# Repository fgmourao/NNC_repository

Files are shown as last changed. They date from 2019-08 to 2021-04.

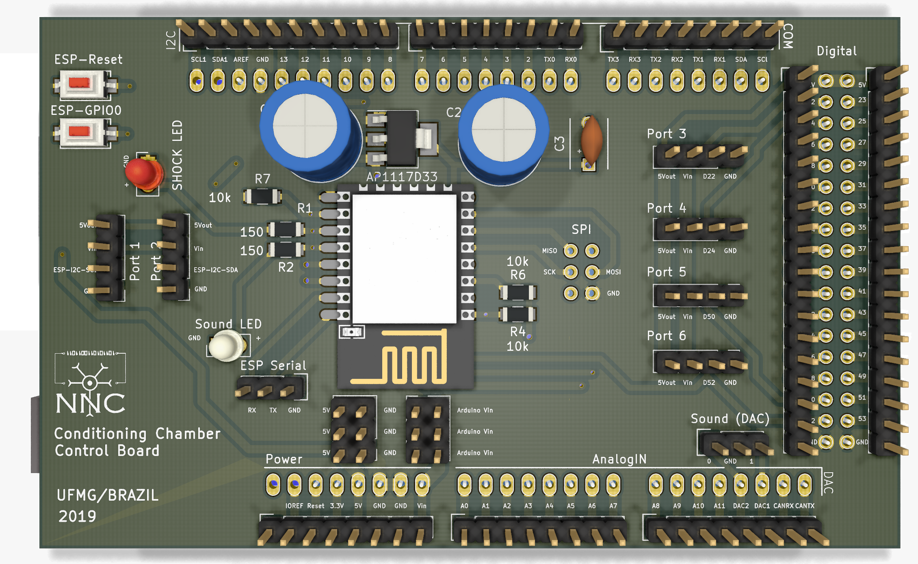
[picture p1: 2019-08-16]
Conditioning Chamber/Hardware/Kicad/Control Board/NNC_ControlBoard.png

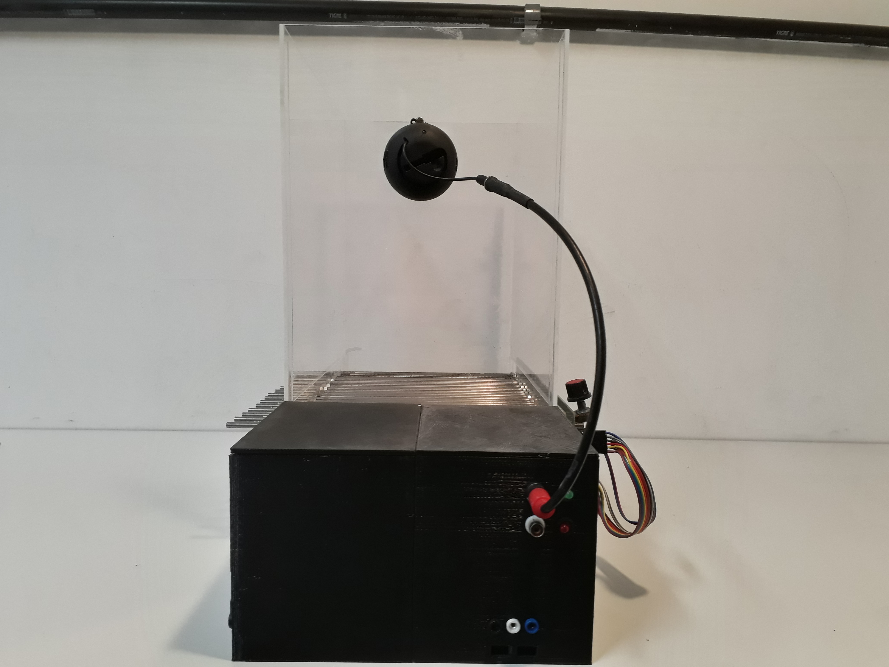
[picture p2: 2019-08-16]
Conditioning Chamber/Images/8.jpg

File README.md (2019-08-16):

# NNC_repository
Custom equipments for open source science. Developed  by the Núcleo de Neurociências (Neuroscience Research Center) at the Federal University of Minas Gerais (Brazil).

Núcleo de Neurociências (Neuroscience Research Center)<br />
Department of Physiology and Biophysics<br />
Institute of Biological Sciences (ICB) <br />
Federal University of Minas Gerais  (UFMG)<br />
Av. Antônio Carlos, 6627 - Postal Code:  31270-901 - Campus Pampulha<br />
Belo Horizonte - MG - Brazil<br />
Phone: +55 31 3409-2930

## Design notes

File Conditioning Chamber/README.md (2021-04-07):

# A Custom Microcontrolled and Wireless-Operated Chamber for Auditory Fear Conditioning

Authors: Paulo Aparecido Amaral Júnior1,2#, Flávio Afonso Gonçalves Mourão1#, Mariana Chamon Ladeira Amâncio1, Hyorrana Pereira Pinto1, Vinícius Rezende Carvalho1,2, Leonardo de Oliveira Guarnieri1,2, Hermes Aguiar Magalhães2, Márcio Flávio Dutra Moraes1*. 

1 - Núcleo de Neurociências, Departamento de Fisiologia e Biofísica, Instituto de Ciências Biológicas (ICB), Universidade Federal de Minas Gerais (UFMG). Av. Antônio Carlos, 6627 - CEP 31270-901. Belo Horizonte, Minas Gerais, Brazil.<br />
2 - Programa de Pós-Graduação em Engenharia Elétrica, Departamento de Engenharia Eletrônica (DELT), Escola de Engenharia, Universidade Federal de Minas Gerais (UFMG). Av. Antônio Carlos, 6627 - CEP 31270-901. Belo Horizonte, Minas Gerais, Brazil.<br />

Animal behavioral paradigms, such as classical conditioning and operant conditioning, are an important tool to study the neural basis of cognition and behavior. These paradigms involve manipulating sensory stimuli in a way that learning processes are induced under controlled experimental conditions. However, the majority of the commercially available equipment did not offer flexibility to manipulate stimuli. Therefore, the development of most versatile devices would allow the study of more complex cognitive functions. The purpose of this work is to present a low-cost, customized and wireless-operated chamber for animal behavior conditioning, based on the joint operation of two microcontroller modules: Arduino Due and ESP8266-12E. Our results showed that the auditory stimulation system allows setting the carrier frequency in the range of 1 Hz up to more than 100 kHz and the sound stimulus can be modulated in amplitude, also over a wide range of frequencies. Likewise, foot-shock could be precisely manipulated regarding its amplitude (from ~200 μA to ~1500 μA) and frequency (up to 20 pulses per second). Finally, adult rats exposed to a protocol of cued fear conditioning in our device showed consistent behavioral response and electrophysiological evoked responses in the midbrain auditory pathway. Furthermore, the device developed in the current study represents an open source alternative to develop customized protocols to study fear memory under conditions of varied sensory stimuli. 

Paper published in Frontiers in Neuroscience | www.frontiersin.org
https://www.frontiersin.org/articles/10.3389/fnins.2019.01193/full

Correspondence:<br />

Flávio Afonso Gonçalves Mourão, PhD<br />
Núcleo de Neurociências, Departamento de Fisiologia e Biofísica<br />
Instituto de Ciências Biológicas (ICB)<br /> 
Universidade Federal de Minas Gerais (UFMG)<br />
Av. Antônio Carlos, 6627 - CEP 31270-901- Campus Pampulha<br />
Belo Horizonte - MG - Brazil<br />
Fax: +55 31 3409-2924 Phone: +55 31 3409-2927<br />
Email: mourao.fg@gmail.com<br />

Márcio Flávio Dutra Moraes, PhD<br />
Núcleo de Neurociências, Departamento de Fisiologia e Biofísica<br />
Instituto de Ciências Biológicas (ICB)<br /> 
Universidade Federal de Minas Gerais (UFMG)<br />
Av. Antônio Carlos, 6627 - CEP 31270-901- Campus Pampulha<br />
Belo Horizonte - MG - Brazil<br />
Fax: +55 31 3409-2924 Phone: +55 31 3409-2930<br />
Email: mfdm@icb.ufmg.br<br />

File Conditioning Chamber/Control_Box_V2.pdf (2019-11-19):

# Control Box V2.0

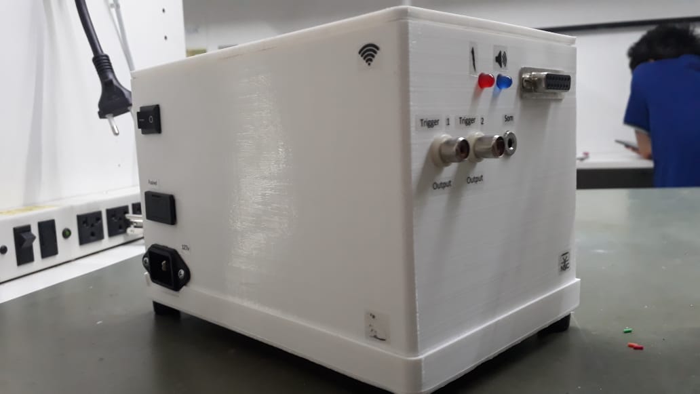
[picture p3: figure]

## Flávio Afonso Gonçalves Mourão NNC/UFMG – 2019 Brazil

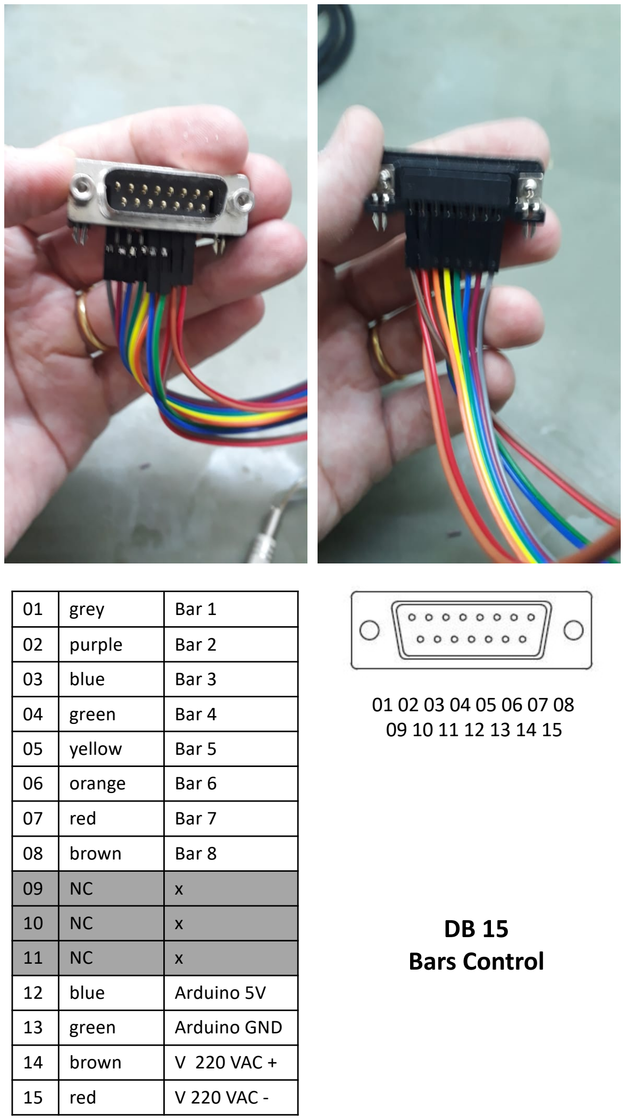
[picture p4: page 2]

01 02 03 04 05 06 07 08
09 10 11 12 13 14 15
01 | grey | Bar 1
02 | purple | Bar 2
03 | blue | Bar 3
04 | green | Bar 4
05 | yellow | Bar 5
06 | orange | Bar 6
07 | red | Bar 7
08 | brown | Bar 8
09 | NC | x
10 | NC | x
11 | NC | x
12 | blue | Arduino 5V
13 | green | Arduino GND
14 | brown | V 220 VAC +
15 | red | V 220 VAC -

DB 15

## Bars Control

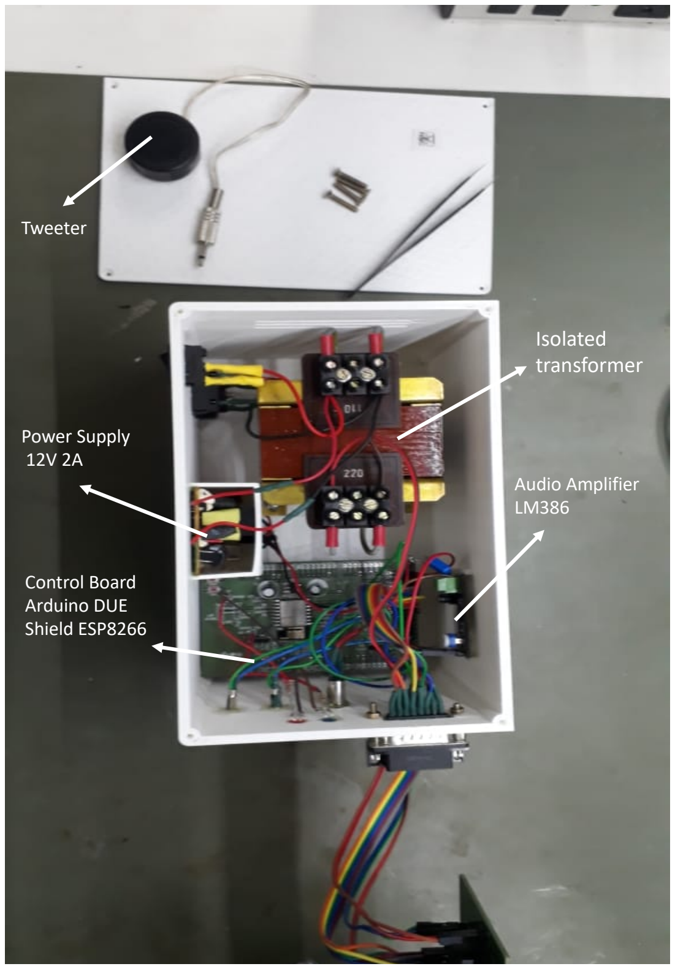
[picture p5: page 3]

## Isolated transformer

### Audio Amplifier

LM386

### Power Supply

12V 2A

### Control Board Arduino DUE Shield ESP8266

### Tweeter

Audio Amplifier
LM386
https://www.amazon.com/5V-12V-Amplifier-Module-Arduino-EK1236/dp/B01FDD3FYQ

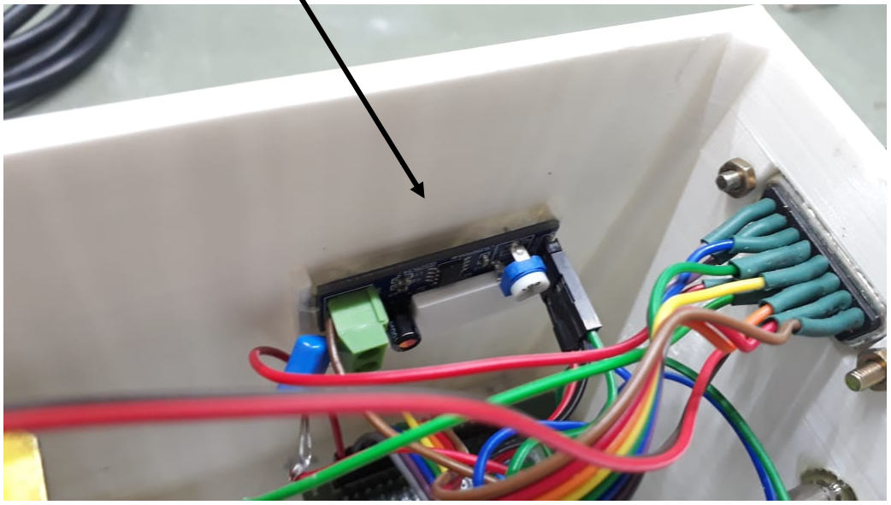
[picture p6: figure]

## 18.4 x 11.6 mm

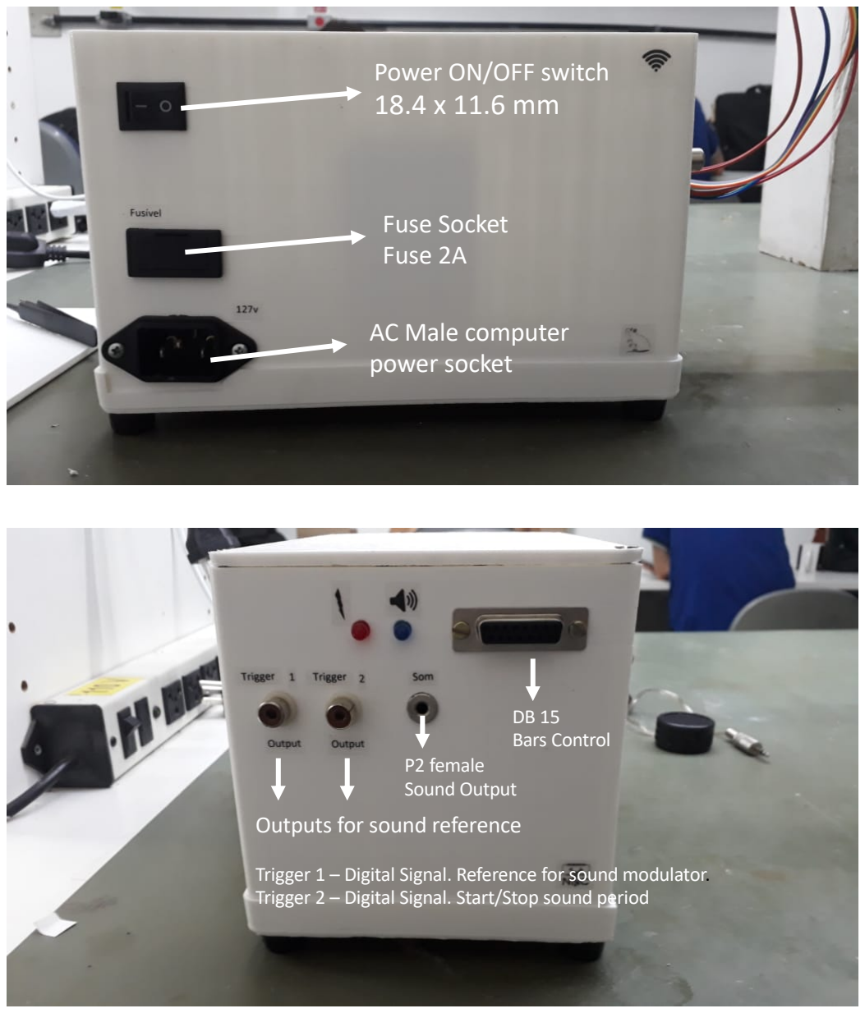
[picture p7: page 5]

### Fuse Socket Fuse 2A

DB 15
Bars Control

Outputs for sound reference

Trigger 1 – Digital Signal. Reference for sound modulator. Trigger 2 – Digital Signal. Start/Stop sound period

### AC Male computer power socket

### Power ON/OFF switch

P2 female
Sound Output

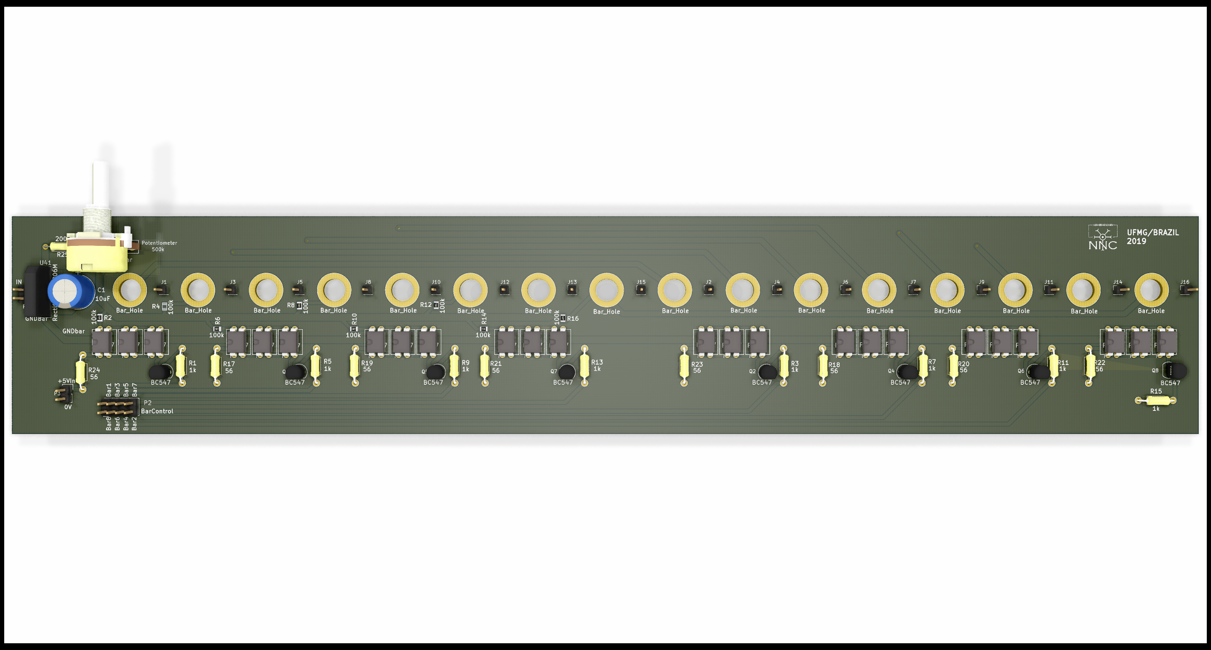
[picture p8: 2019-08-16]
Conditioning Chamber/Hardware/Kicad/Shock Board/NNC_ShockBoard.png

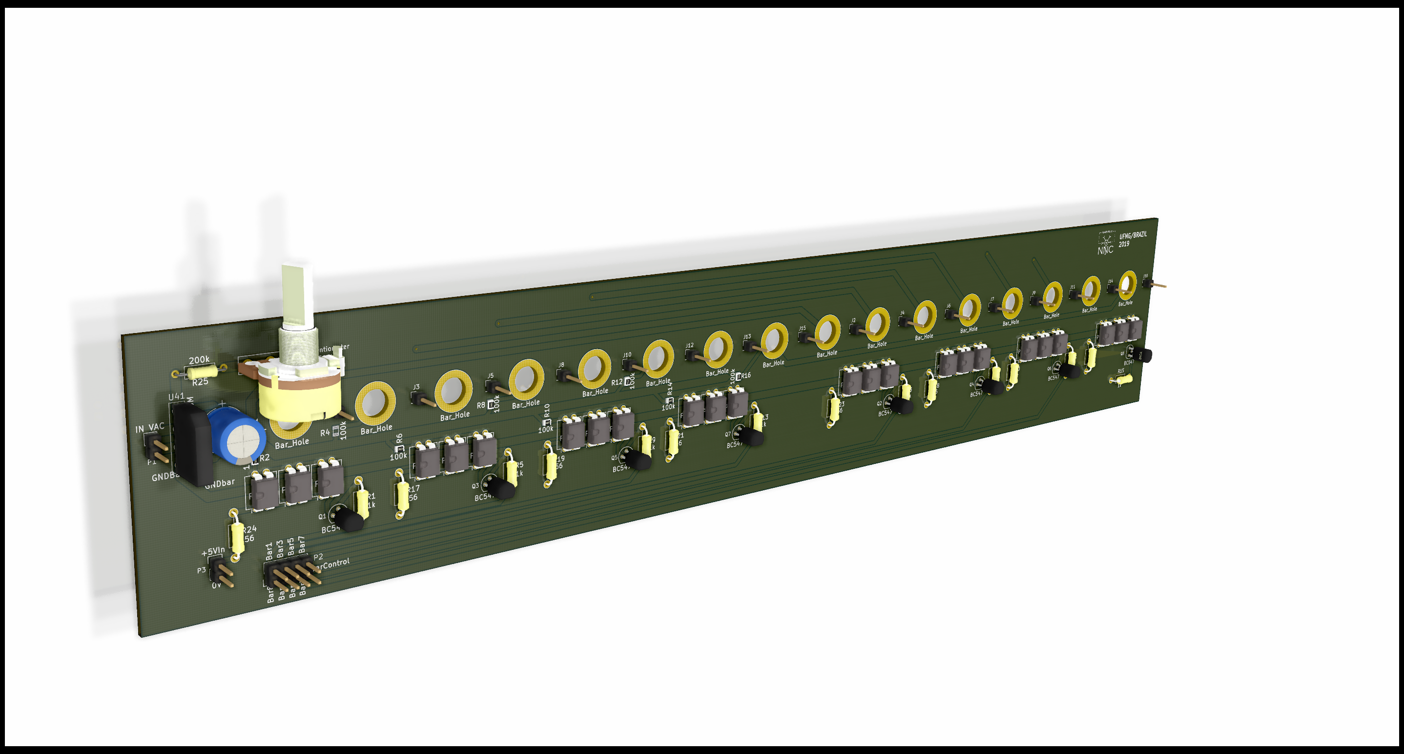
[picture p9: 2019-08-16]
Conditioning Chamber/Hardware/Kicad/Shock Board/NNC_ShockBoard1.png

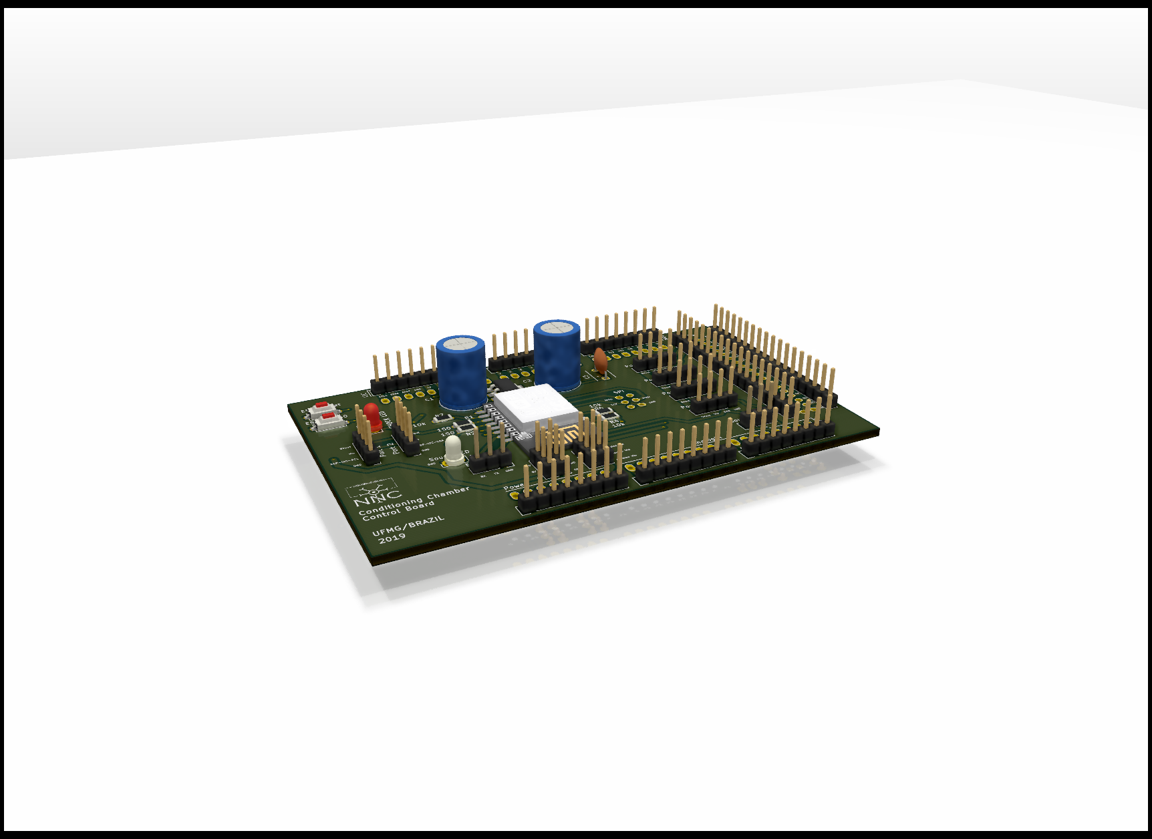
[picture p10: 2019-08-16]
Conditioning Chamber/Hardware/Kicad/Control Board/NNC_ControlBoard2.png

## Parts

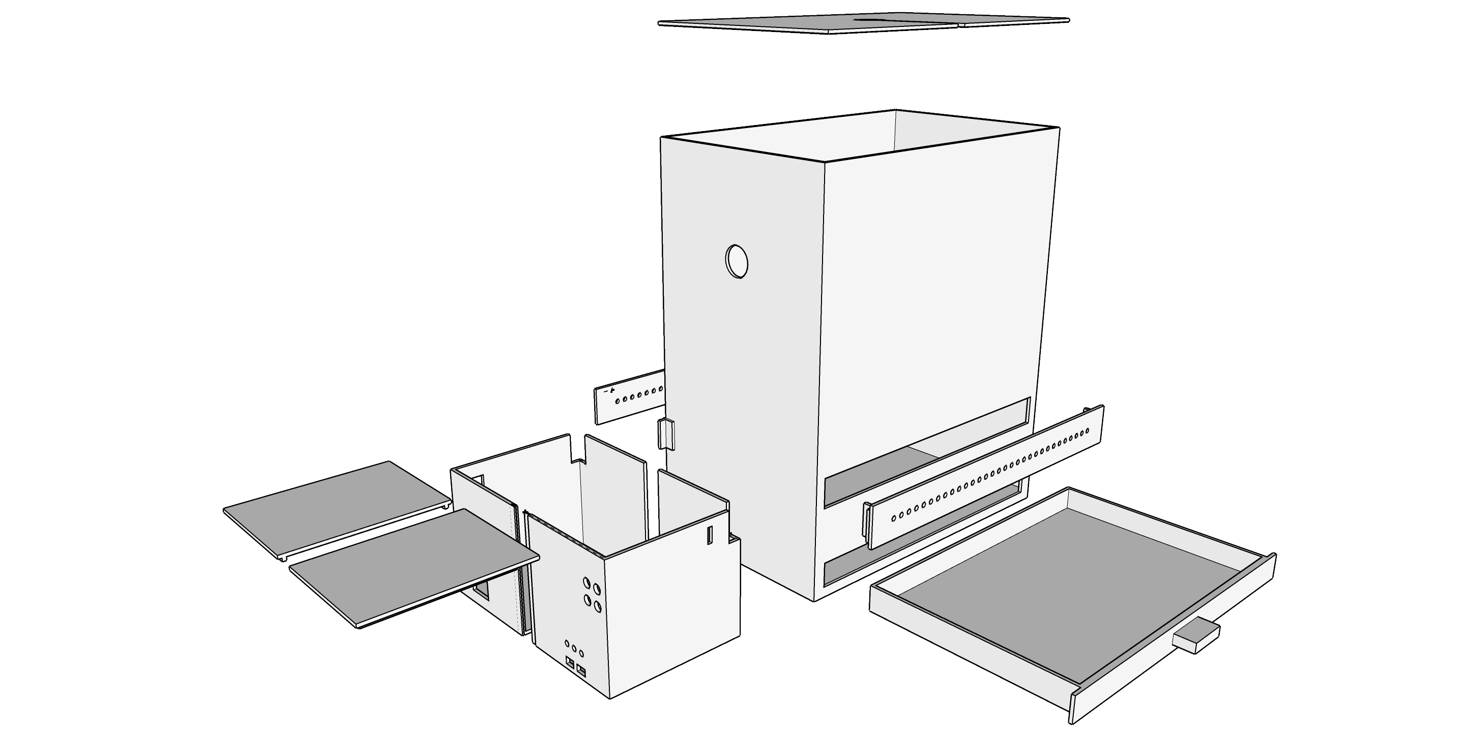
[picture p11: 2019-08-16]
Conditioning Chamber/Hardware/3D/Conditioning_Chamber/png/Conditioning_full_parts.png

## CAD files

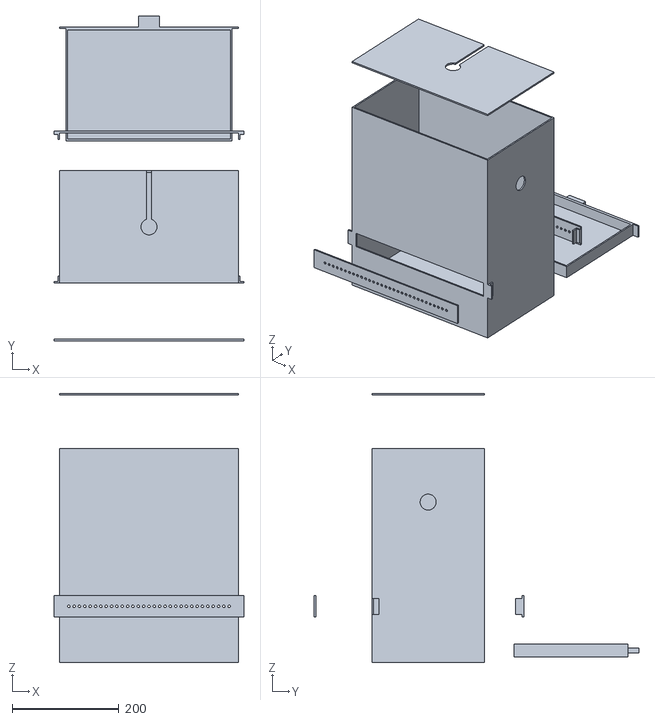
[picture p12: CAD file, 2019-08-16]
Conditioning Chamber/Hardware/3D/Conditioning_Chamber/Stl/Chamber/Full_Chamber.stl
355.0 x 607.0 x 503.0

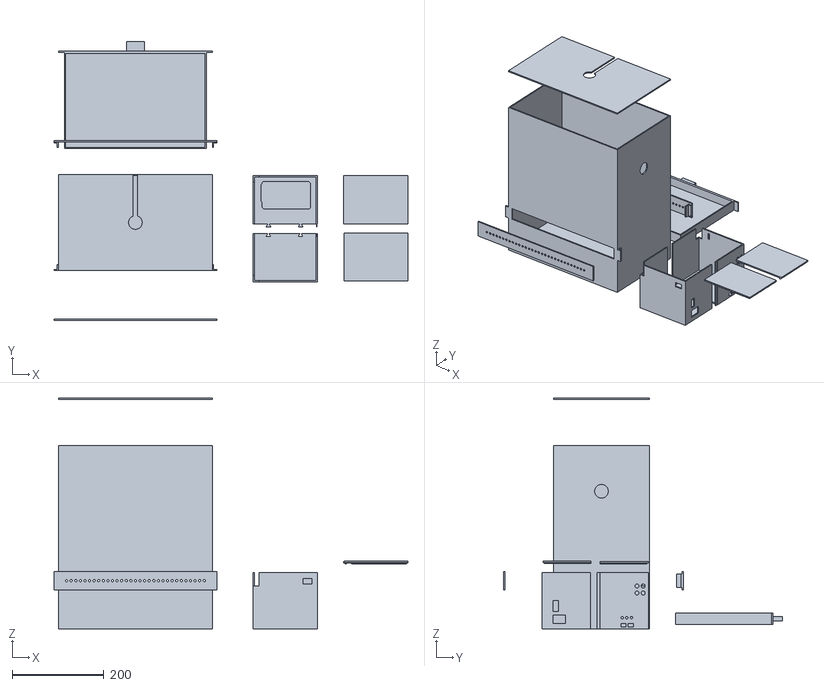
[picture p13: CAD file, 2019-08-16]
Conditioning Chamber/Hardware/3D/Conditioning_Chamber/Stl/Chamber/Conditioning_full_parts.stl
771.6 x 607.0 x 503.0

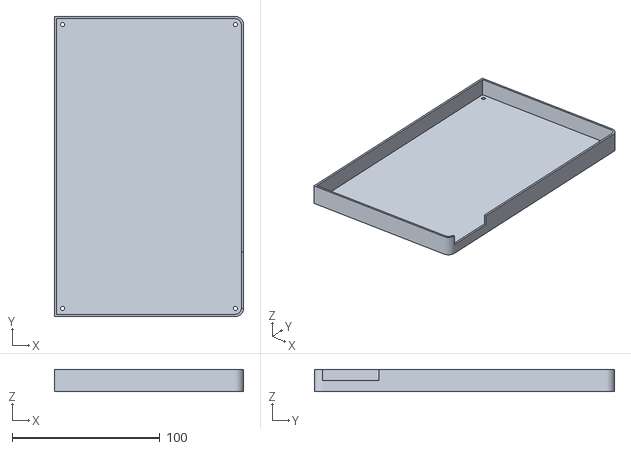
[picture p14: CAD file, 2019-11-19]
Conditioning Chamber/Hardware/3D/Conditioning_Chamber/Stl/Control_box_V2/Control_box_floor.stl
128.0 x 203.0 x 15.0

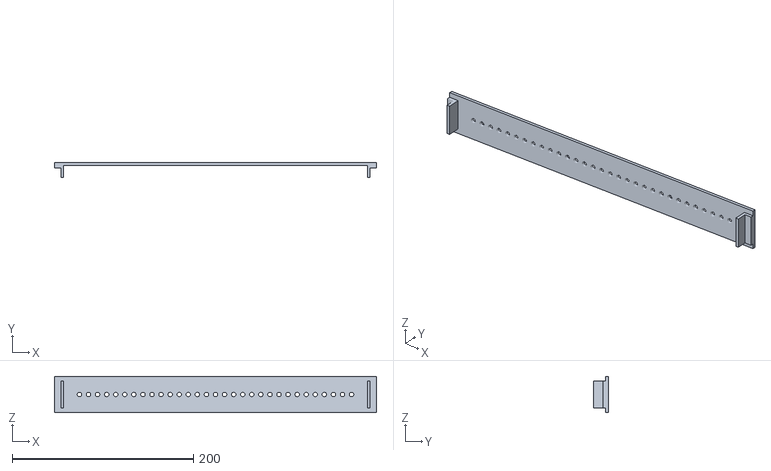
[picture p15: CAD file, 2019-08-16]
Conditioning Chamber/Hardware/3D/Conditioning_Chamber/Stl/Chamber/Holder_bars1.stl
355.0 x 16.0 x 40.0

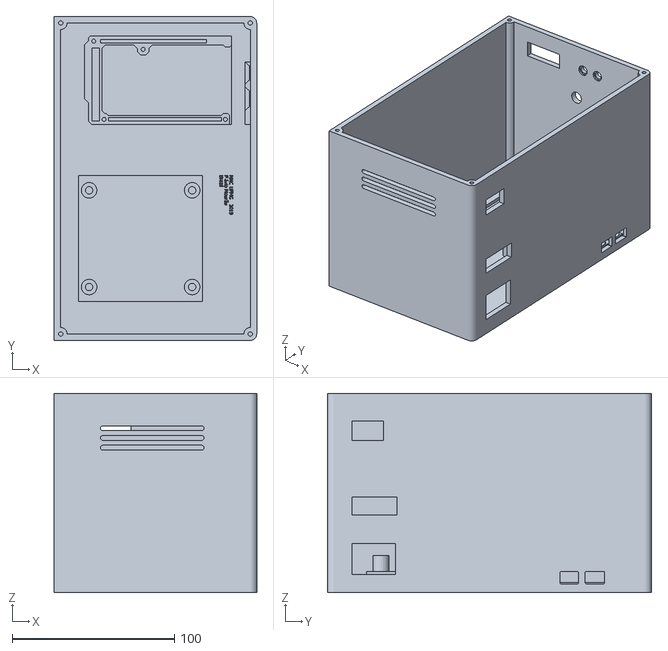
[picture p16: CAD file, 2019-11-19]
Conditioning Chamber/Hardware/3D/Conditioning_Chamber/Stl/Control_box_V2/Control_box.stl
125.0 x 200.0 x 123.0

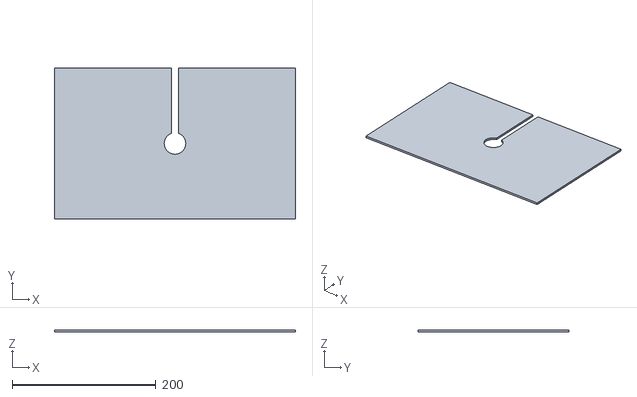
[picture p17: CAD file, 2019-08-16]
Conditioning Chamber/Hardware/3D/Conditioning_Chamber/Stl/Chamber/Cover.stl
335.0 x 210.0 x 3.00

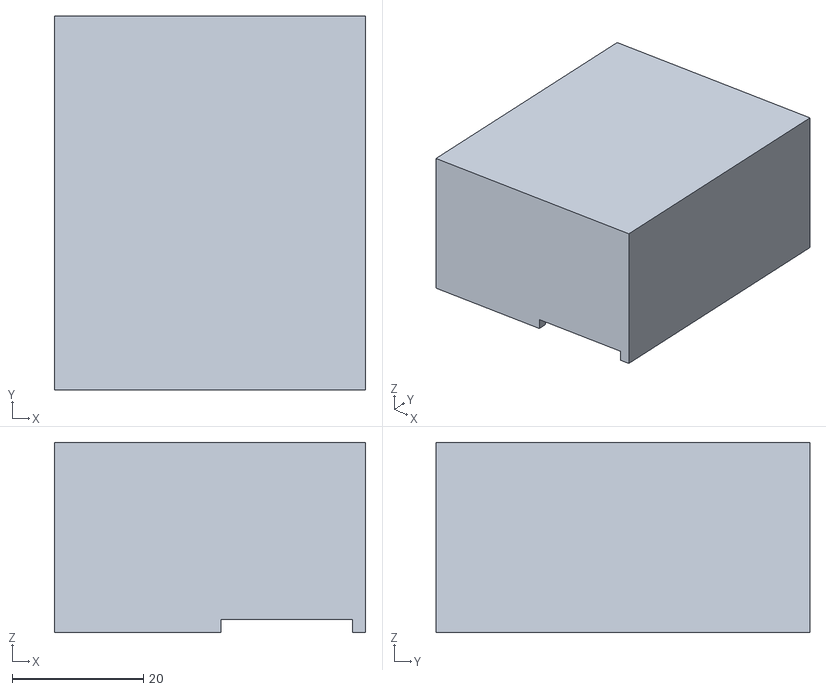
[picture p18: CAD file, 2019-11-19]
Conditioning Chamber/Hardware/3D/Conditioning_Chamber/Stl/Control_box_V2/Power_supply_holder.stl
47.4 x 57.0 x 29.0

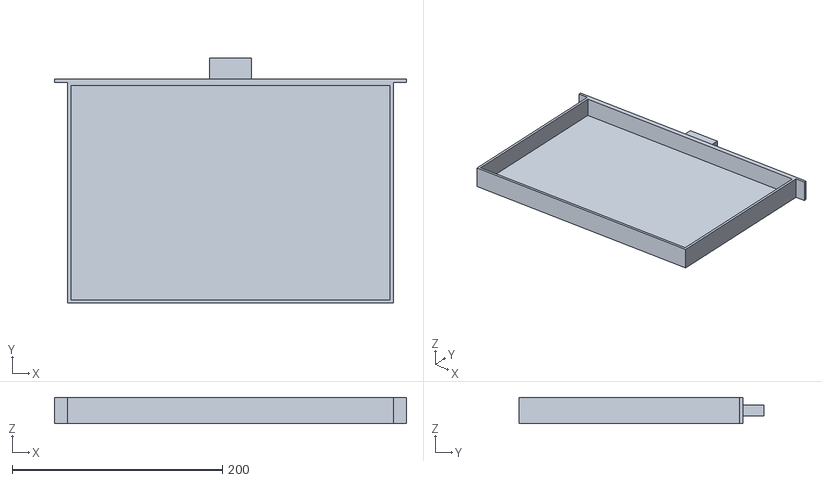
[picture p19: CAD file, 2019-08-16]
Conditioning Chamber/Hardware/3D/Conditioning_Chamber/Stl/Chamber/Botton.stl
335.0 x 233.0 x 25.0

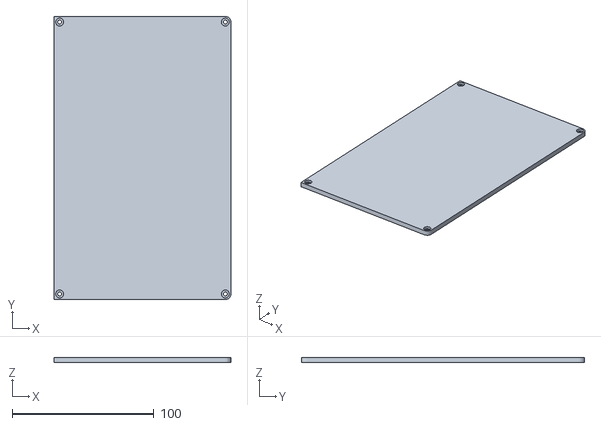
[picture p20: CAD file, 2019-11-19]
Conditioning Chamber/Hardware/3D/Conditioning_Chamber/Stl/Control_box_V2/Control_box_roof.stl
125.0 x 200.0 x 3.80

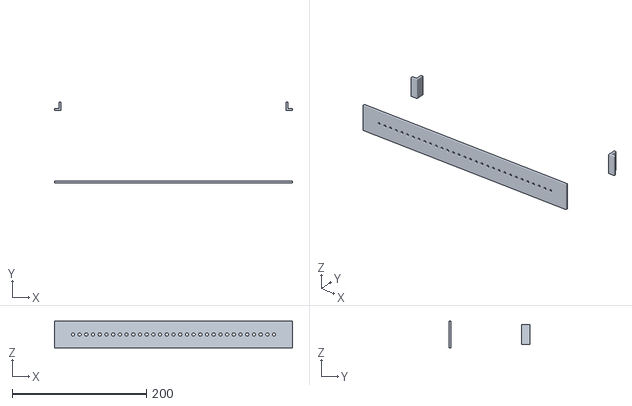
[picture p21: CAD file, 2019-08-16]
Conditioning Chamber/Hardware/3D/Conditioning_Chamber/Stl/Chamber/Holder_bars2.stl
355.0 x 121.0 x 40.0

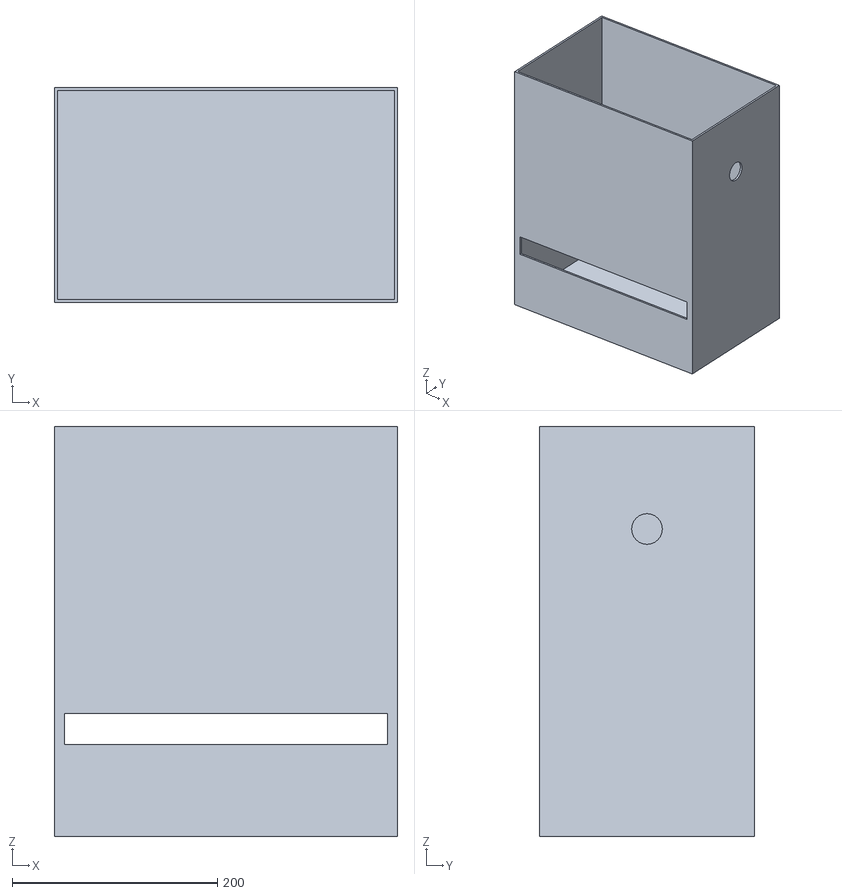
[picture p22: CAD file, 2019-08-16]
Conditioning Chamber/Hardware/3D/Conditioning_Chamber/Stl/Chamber/Chamber.stl
335.0 x 210.0 x 400.0

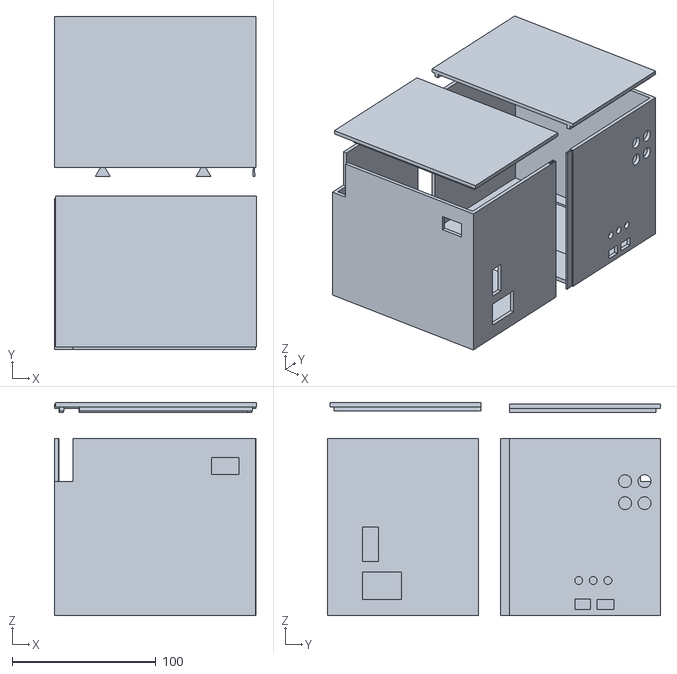
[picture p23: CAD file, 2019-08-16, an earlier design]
Conditioning Chamber/Hardware/3D/Conditioning_Chamber/Stl/Control_box_V1/Control_box_Full_parts.stl
140.7 x 231.5 x 148.1

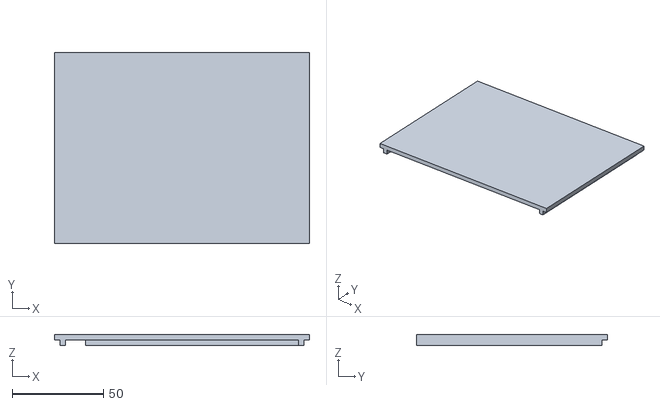
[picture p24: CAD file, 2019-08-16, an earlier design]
Conditioning Chamber/Hardware/3D/Conditioning_Chamber/Stl/Control_box_V1/Control_box_cover_right.stl
140.0 x 105.0 x 6.00

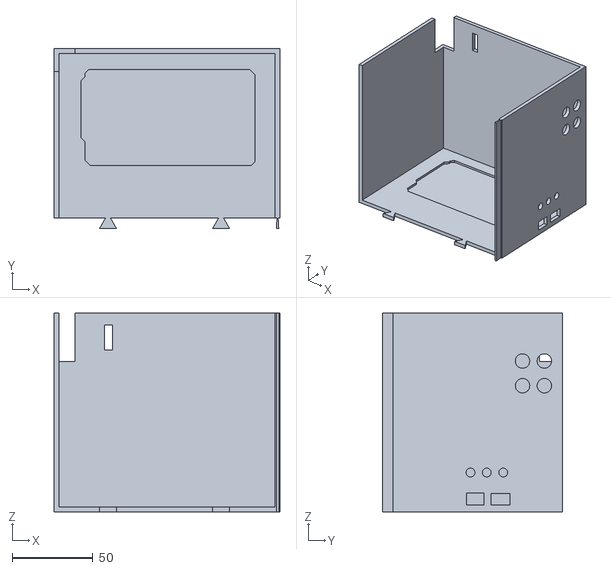
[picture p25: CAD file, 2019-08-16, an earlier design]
Conditioning Chamber/Hardware/3D/Conditioning_Chamber/Stl/Control_box_V1/Control_box_right.stl
140.0 x 111.2 x 123.0

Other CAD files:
Conditioning Chamber/Hardware/3D/Conditioning_Chamber/dwg/Chamber/Full_Chamber_measurements.dwg
Conditioning Chamber/Hardware/3D/Conditioning_Chamber/dwg/Chamber/drawer.dwg
Conditioning Chamber/Hardware/3D/Conditioning_Chamber/dwg/Chamber/holder_bars.dwg
Conditioning Chamber/Hardware/3D/Conditioning_Chamber/dwg/Chamber/roof.dwg
Conditioning Chamber/Hardware/3D/Conditioning_Chamber/Stl/Control_box_V1/Control_box_cover_left.stl
Conditioning Chamber/Hardware/3D/Conditioning_Chamber/Stl/Control_box_V1/Control_box_left.stl
Conditioning Chamber/Hardware/3D/Conditioning_Chamber/dwg/Chamber/chamber.dwg
Conditioning Chamber/Hardware/3D/Conditioning_Chamber/obj/Chamber/Conditioning_full_parts.obj
Conditioning Chamber/Hardware/3D/Conditioning_Chamber/skp/Chamber/Full_Chamber.skp
Conditioning Chamber/Hardware/3D/Conditioning_Chamber/skp/Control_box_V1/Control_box_full.skp
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

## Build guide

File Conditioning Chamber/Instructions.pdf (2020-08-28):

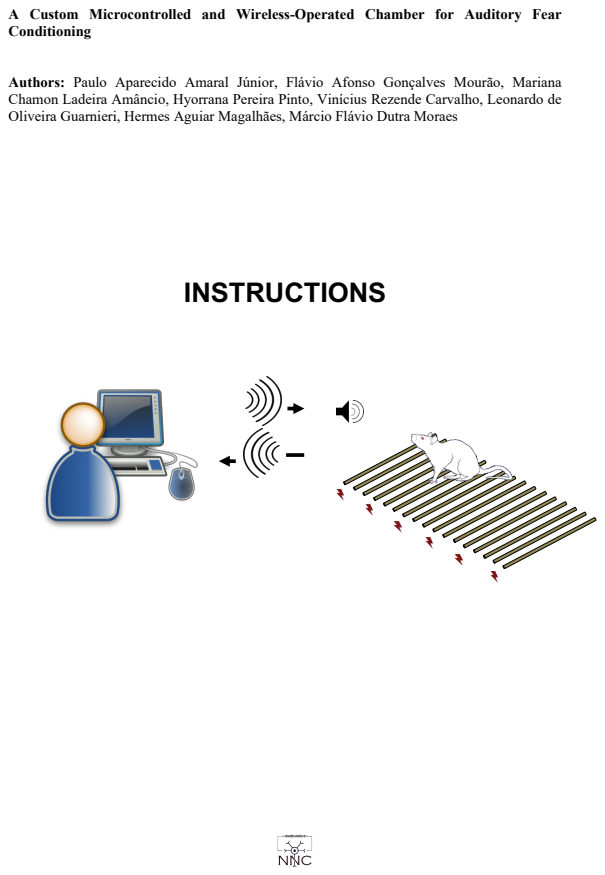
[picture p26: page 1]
INSTRUCTIONS

A Custom Microcontrolled and Wireless-Operated Chamber for Auditory Fear
Conditioning

Authors: Paulo Aparecido Amaral Júnior, Flávio Afonso Gonçalves Mourão, Mariana
Chamon Ladeira Amâncio, Hyorrana Pereira Pinto, Vinícius Rezende Carvalho, Leonardo de
Oliveira Guarnieri, Hermes Aguiar Magalhães, Márcio Flávio Dutra Moraes

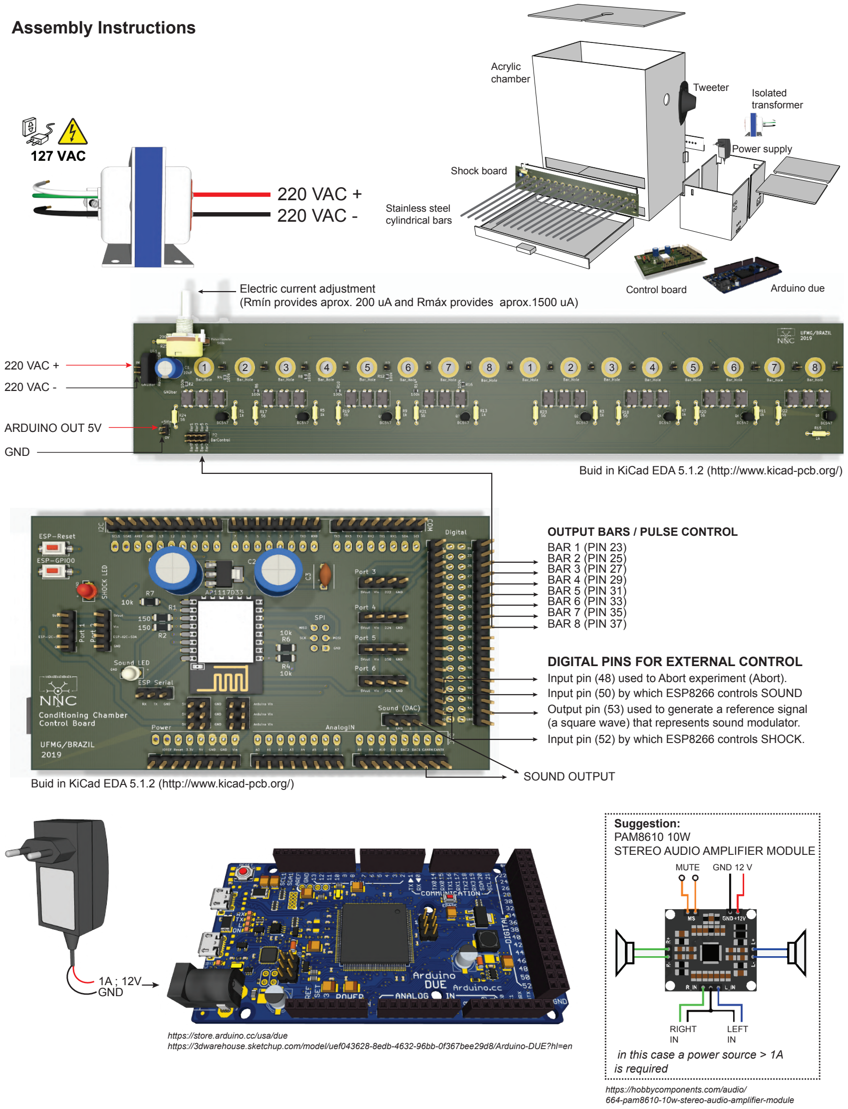
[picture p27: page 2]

BAR 1 (PIN 23)
BAR 2 (PIN 25)
BAR 3 (PIN 27)
BAR 4 (PIN 29)
BAR 5 (PIN 31)
BAR 6 (PIN 33)
BAR 7 (PIN 35)
BAR 8 (PIN 37)

Output pin (53) used to generate a reference signal (a square wave) that represents sound modulator.

Input pin (50) by which ESP8266 controls SOUND

Input pin (48) used to Abort experiment (Abort).

Input pin (52) by which ESP8266 controls SHOCK.

SOUND OUTPUT

ARDUINO OUT 5V

220 VAC +

Electric current adjustment
(Rmín provides aprox. 200 uA and Rmáx provides aprox.1500 uA)

220 VAC +
220 VAC -

GND

1A ; 12V

in this case a power source > 1A is required

220 VAC -

GND

Suggestion:
PAM8610 10W
STEREO AUDIO AMPLIFIER MODULE

MUTE GND 12 V

RIGHT
IN

LEFT
IN

https://hobbycomponents.com/audio/664-pam8610-10w-stereo-audio-amplifier-modulehttps://store.arduino.cc/usa/duehttps://3dwarehouse.sketchup.com/model/uef043628-8edb-4632-96bb-0f367bee29d8/Arduino-DUE?hl=en

DIGITAL PINS FOR EXTERNAL CONTROL

OUTPUT BARS / PULSE CONTROL

Assembly Instructions

Control board | Arduino due

Shock board

Acrylic
chamber

Stainless steel
cylindrical bars

Isolated
transformer

Tweeter

Power supply

1 | 2 | 3 | 4 | 5 | 6 | 7 | 8 | 1 | 2 | 3 | 4 | 5 | 6 | 7 | 8

Buid in KiCad EDA 5.1.2 (http://www.kicad-pcb.org/)

Buid in KiCad EDA 5.1.2 (http://www.kicad-pcb.org/)

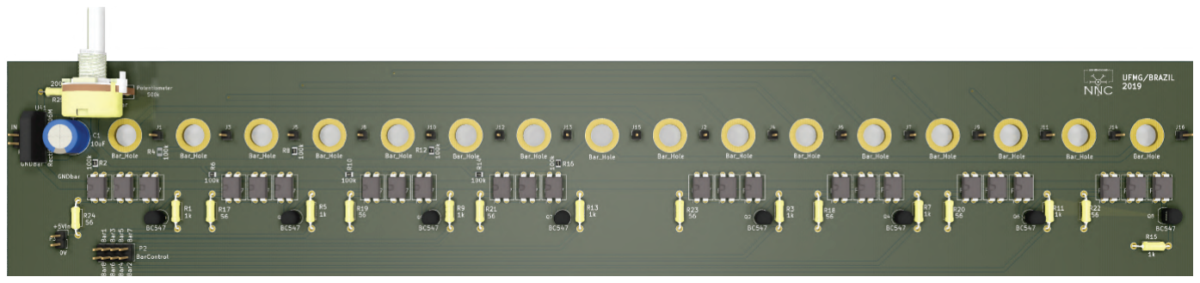
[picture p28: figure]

1 | 2 | 3 | 4 | 5 | 6 | 7 | 8 | 1 | 2 | 3 | 4 | 5 | 6 | 7 | 8

Original bar configuration for experiments with rats

short circuit on the printed circuit board

20 mm

Bar numbers

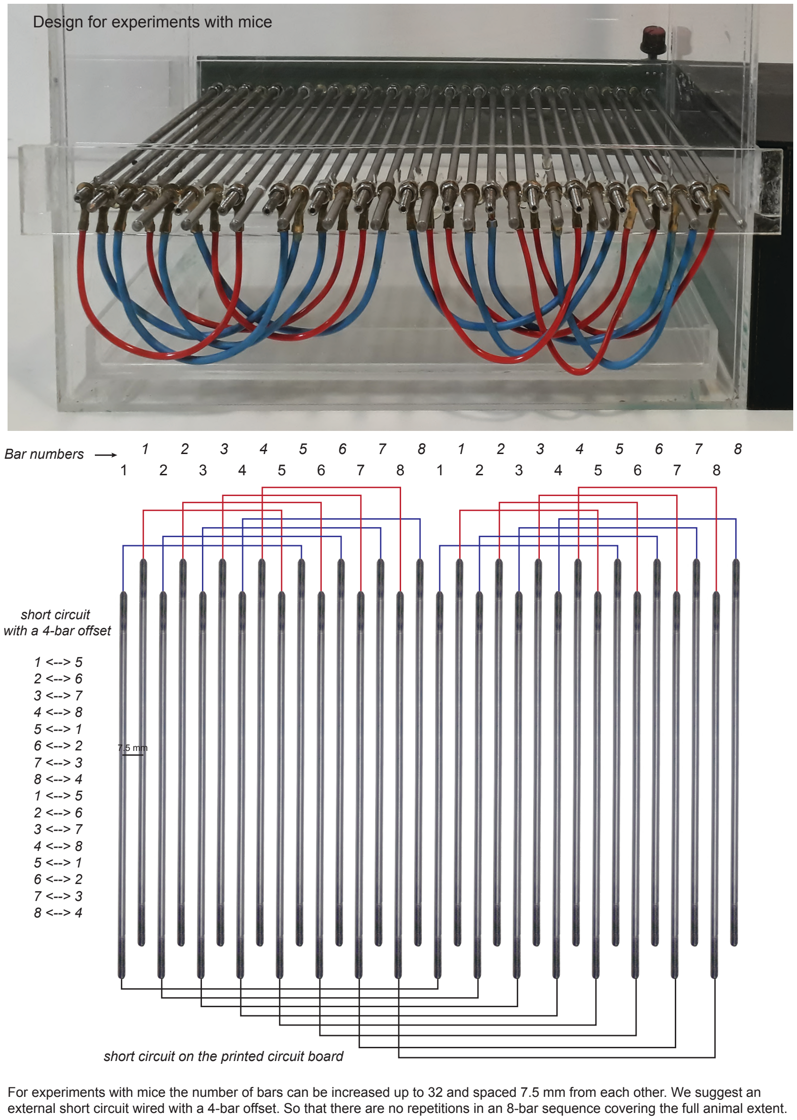
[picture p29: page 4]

1 | 2 | 3 | 4 | 5 | 6 | 7 | 8 | 1 | 2 | 3 | 4 | 5 | 6 | 7 | 8
1 | 2 | 3 | 4 | 5 | 6 | 7 | 8 | 1 | 2 | 3 | 4 | 5 | 6 | 7 | 8

short circuit on the printed circuit board

short circuit
with a 4-bar offset

Bar numbers

1 <--> 5
2 <--> 6
3 <--> 7
4 <--> 8
5 <--> 1
6 <--> 2
7 <--> 3
8 <--> 4
1 <--> 5
2 <--> 6
3 <--> 7
4 <--> 8
5 <--> 1
6 <--> 2
7 <--> 3
8 <--> 4

7.5 mm

For experiments with mice the number of bars can be increased up to 32 and spaced 7.5 mm from each other. We suggest an external short circuit wired with a 4-bar offset. So that there are no repetitions in an 8-bar sequence covering the full animal extent.

Design for experiments with mice

Power Supply

Component | Specification | Quantity
Isolated Transformer | 0.03KVA; 127VAC:220VAC | 1
Power Supply | 1A; 12V | 1

Two-layer printed circuit board with control circuit. It has ESP8266-12E footprint and an Arduino Due shield

Component | | Quantity
Arduino DUE | https://store.arduino.cc/usa/due | 1
Module WI-FI ESP8266-12E | https://www.adafruit.com/product/2491 | 1
FTDI Serial TTL-232 USB | https://www.adafruit.com/product/70 | 1
*TOP | *BOTTOM

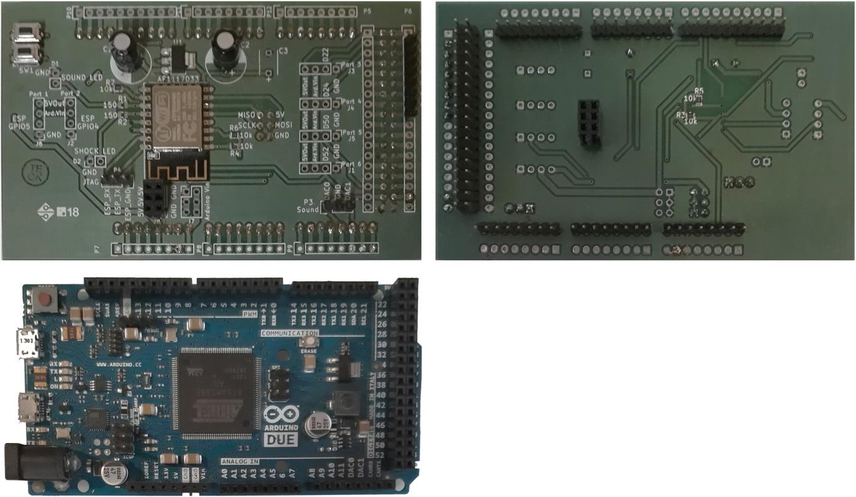
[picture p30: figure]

Component | Model | Specification | Quantity
LDO Voltage Regulators | AP1117D33 | | 1
Radial Electrolytic Capacitor | | 147uF, 550V | 2
Resistor SMD | 10kW 1% | 4
Ceramic Capacitor | | 47uF, 50V | 1
SMD Tactile Push button / Key Switch
(2 x 6 x 2.5 mm)
| KFC-A06 | | 2
Male Pin Headers 2.54mm single (1 x 3 pins) | | | 8
Male Pin Headers 2.54mm single (1 x 4 pins) | | | 6
Male Pin Headers 2.54mm single (1 x 8 pins) | | | 5
Male Pin Headers 2.54mm single (1 x 10 pins) Female Pin Headers 2.54mm single (2 x 3 pins) | | | 1
| | | 1
Dual Pin Headers 2.54mm single (2 x 18 pins) | | | 1

Two-layer printed circuit board with power circuit. Attached to the chamber via 16 mounting holes, this board allows creating electric potential between the conductive bars.

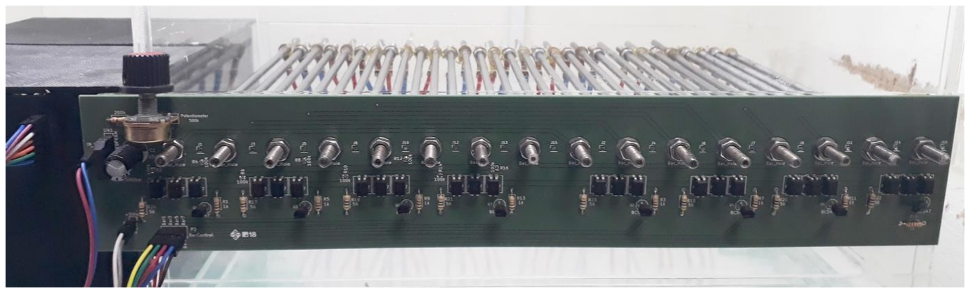
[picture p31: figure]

Component | Model | Specification | Quantity
Resistor Through-hole | | 56W 5% 1/4W | 8
Resistor Through-hole | | 1kW 5% 1/4W | 8
Resistor Through-hole | | 200kW 5% 1/4W | 1
Resistor SMD | | 100kW 1% 1/4W | 8
Potentiometer -Type B Linear response curve | | 500kW | 1
Radial Electrolytic Capacitor | | 10uF, 350V | 1
Bridge Rectifier Diode | 2KBP06M | 2600V, 2A. | 1
Optocouplers | PC817 4-pin | - | 24
Transistors | BC547B | - | 8
Pin Headers 2.54mm single (1 x 12 pins) | | | 1
Dual Pin Headers 2.54mm single (2 x 4 pins) | | | 1
Pin Headers 2.54mm single (1 x 2 pins) | | | 2
Female Jumper wires | | | 12

Stainless steel cylindrical bar and hex nuts

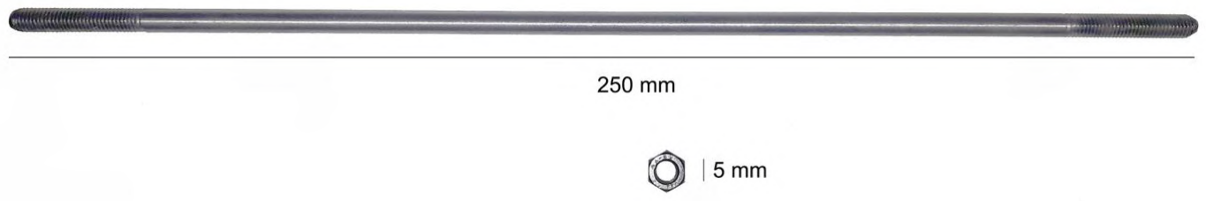
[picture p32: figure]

Component | | Quantity
Stainless steel cylindrical bars | 250 x 5 mm | 32 (or 64)
Stainless steel hex nuts | 5 mm | 64 (or 128)

Printed circuit boards with its components map

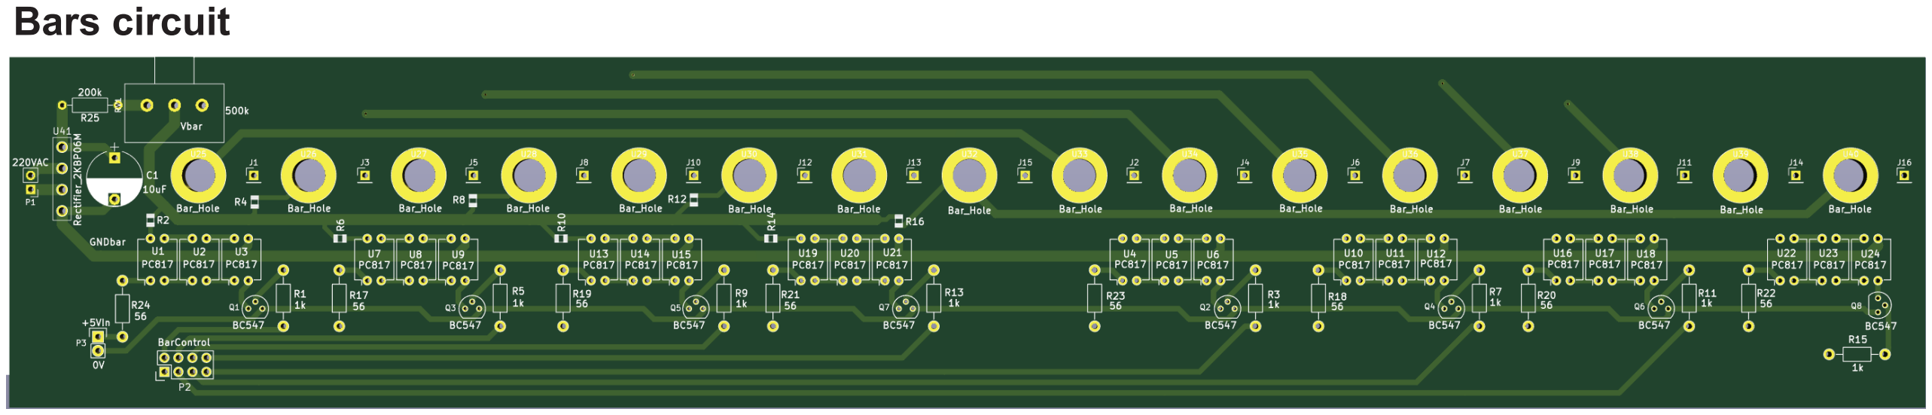
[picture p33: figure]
Bars circuit

Legend:

. P1 - Isolated transformer input
. P2 - Bar control input
. P3 - Input from Arduino output 5V . U1 -> U24 - Optocouplers PC817
. U41 - Bridge Rectifier Diode
. Q1 -> Q8 - Transistors BC547B
. R2,R4,R6,R8,R10,R12,R14,R16 - Resistor SMD 100k1 . R1,R3,R5,R7,R9,R11,R13,R15 - Resistor SMD 1k1
. R17 - R24 - Resistor SMD 561
. R25 - 200k1
. C1 - Radial Electrolytic Capacitor 10uF, 350V
. J1 -> J16 - Pins for current test
. No stamp - upper left corner - Potentiometer, Type B Linear response curve, 500k1

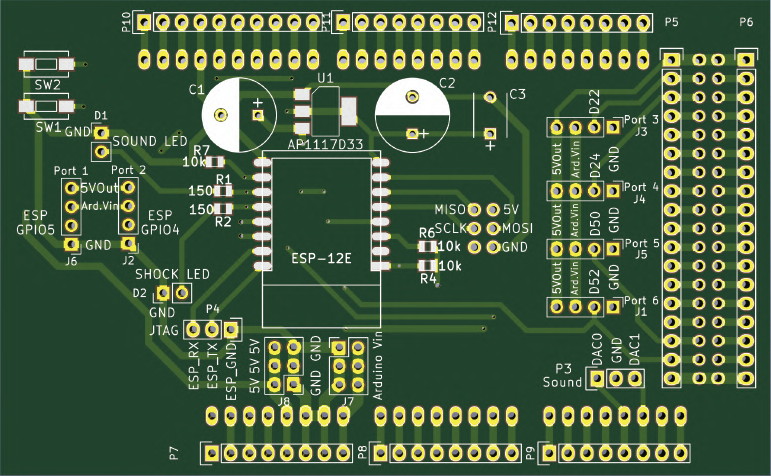
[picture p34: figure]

Legend:

. P3 - Arduino Digital-Analogic converter ports for sound output (Default DAC1)
. P4 - Serial port to program ESP8266. GND, TX (Transmit) and RX(Receive)

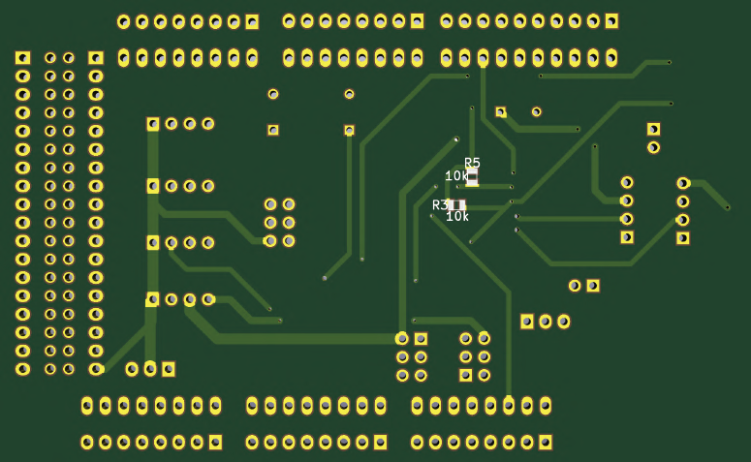
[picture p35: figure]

. P5 -> P12 - Pin Headers that will connect to the Arduino board. Need to be welded underneath.
. Port1 - Port6 - Generic Arduino/ESP8266 outputs (5v out, GND, Arduino in, ESP GPIO04/05, Digital out) . J8 - Generic Arduino outputs (5v out, GND)
. J7 - Generic Arduino outputs (GND, Arduino Vin)
. D1 - LED signaling sound on
. D2 - LED signaling shock on
. SW1 -> SW2 - SMD Tactile Push button to put ESP8266 into programming mode (Hold down the GPIO 0 button -- > Press the Reset button -- > Then let go of both buttons). *SW1 - GPIO 0
*SW2 - Reset
. R1, R2 - Resistor SMD ~1501
. R3 (bottom), R4 (top), R5 (bottom), R6 (top), R7 (top) - Resistor SMD 10k1 . U1 - LDO Voltage Regulator
. C1, C2 - Radial Electrolytic Capacitor 147uF, 550V.
. C3 - Ceramic Capacitor 47uF, 50V
. In the center of the circuit to the right side of the ESP8266 - Female Pin Headers that will connect to the Arduino board (MISO/SCLK/5V/MOSI/GND). Need to be welded underneath.

Control circuit to be attached on Arduino shield

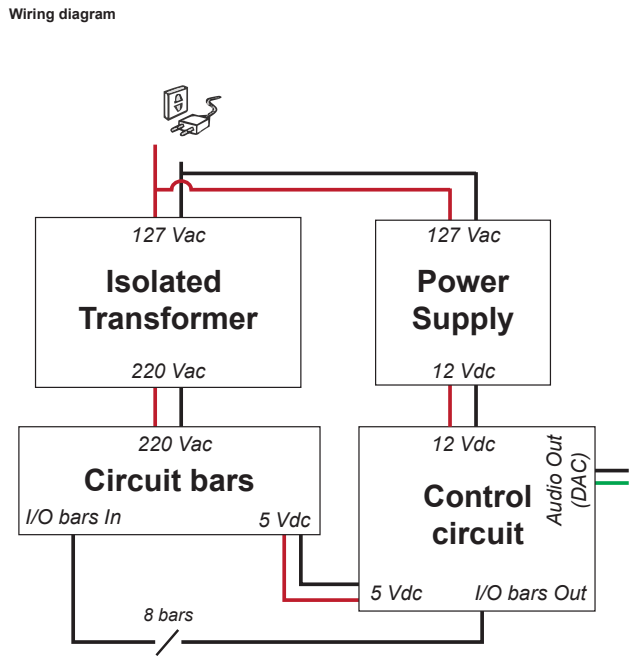
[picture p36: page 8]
5 Vdc; 220 Vac; I/O bars In; Circuit bars; Control; circuit; Isolated Transformer; 127 Vac; Power Supply; 12 Vdc; 8 bars; Wiring diagram

12 Vdc
I/O bars Out Audio Out (DAC⁾

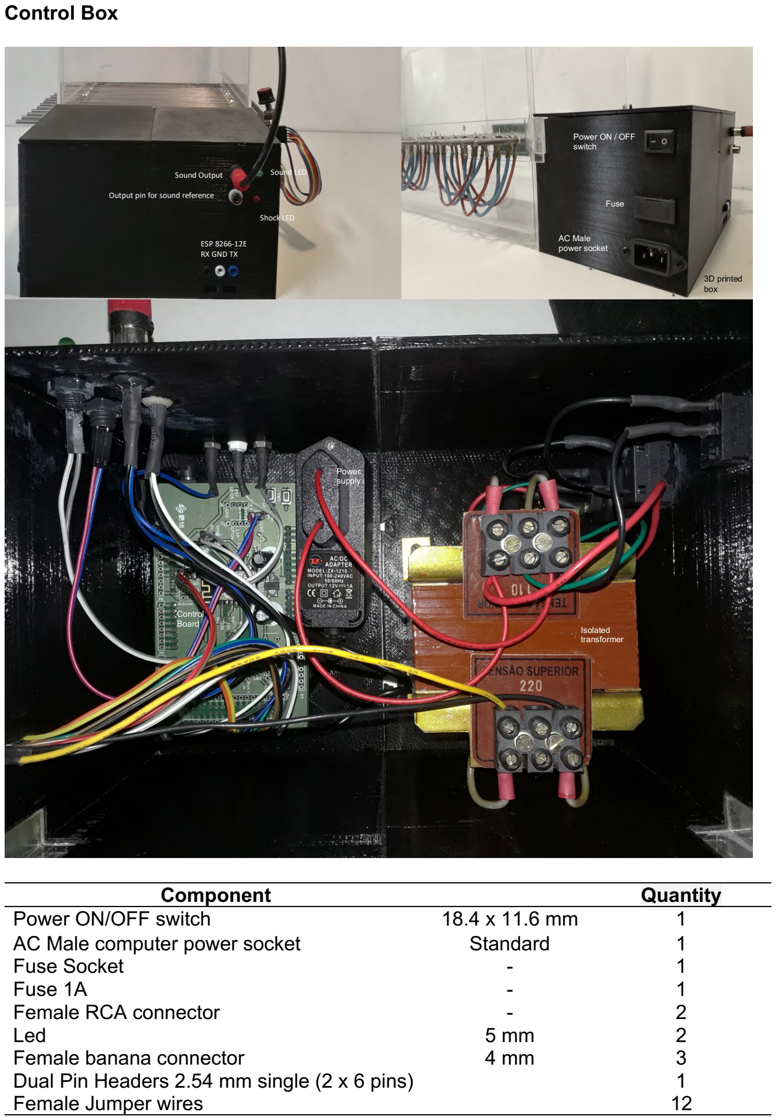
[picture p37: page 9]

Control Box

Component | | Quantity
Power ON/OFF switch | 18.4 x 11.6 mm | 1
AC Male computer power socket | Standard | 1
Fuse Socket | - | 1
Fuse 1A | - | 1
Female RCA connector | - | 2
Led | 5 mm | 2
Female banana connector | 4 mm | 3
Dual Pin Headers 2.54 mm single (2 x 6 pins) | | 1
Female Jumper wires | | 12

ESP 8266-12E
RX GND TX
Sound Output | Sound LED

Shock LED

Output pin for sound reference

Isolated
transformer

Power
supply

Control
Board

Power ON / OFF
switch

Fuse

AC Male
power socket

3D printed
box

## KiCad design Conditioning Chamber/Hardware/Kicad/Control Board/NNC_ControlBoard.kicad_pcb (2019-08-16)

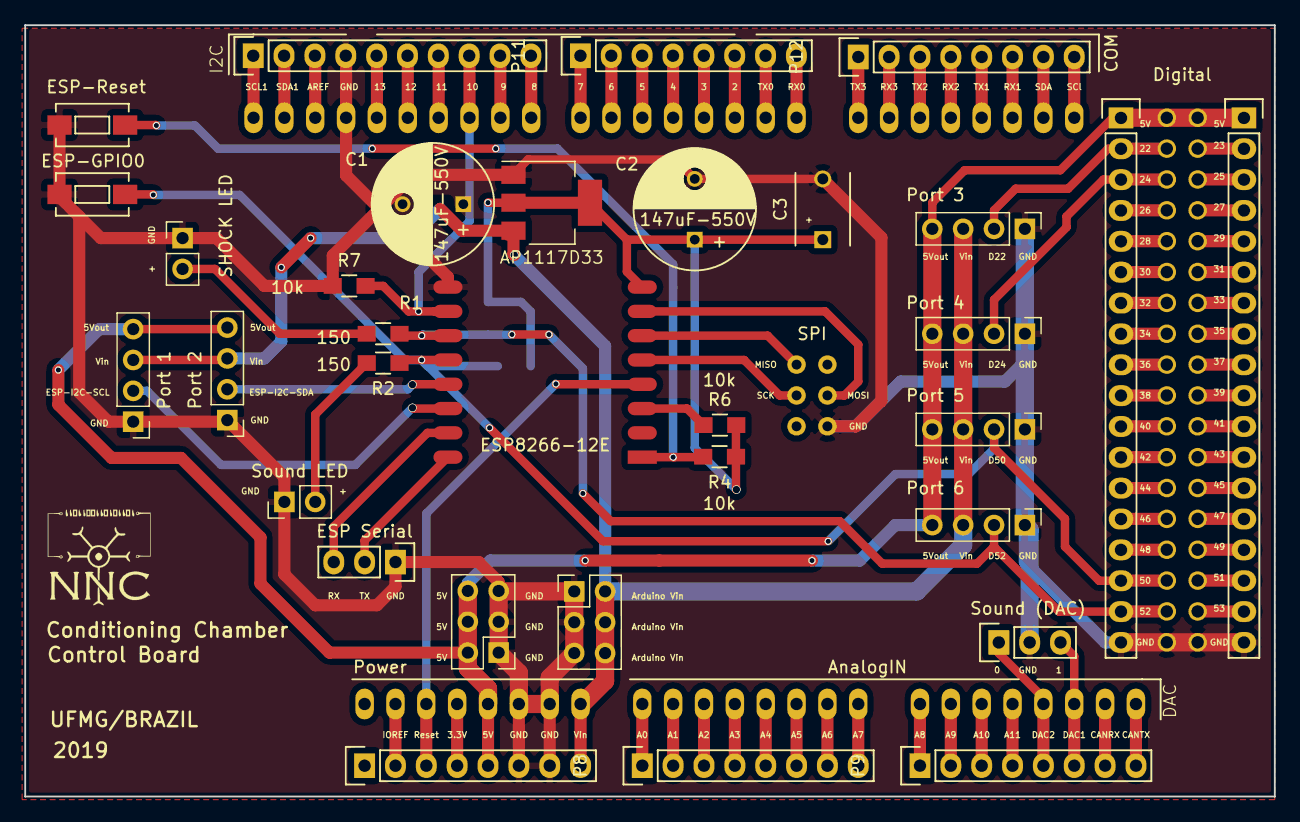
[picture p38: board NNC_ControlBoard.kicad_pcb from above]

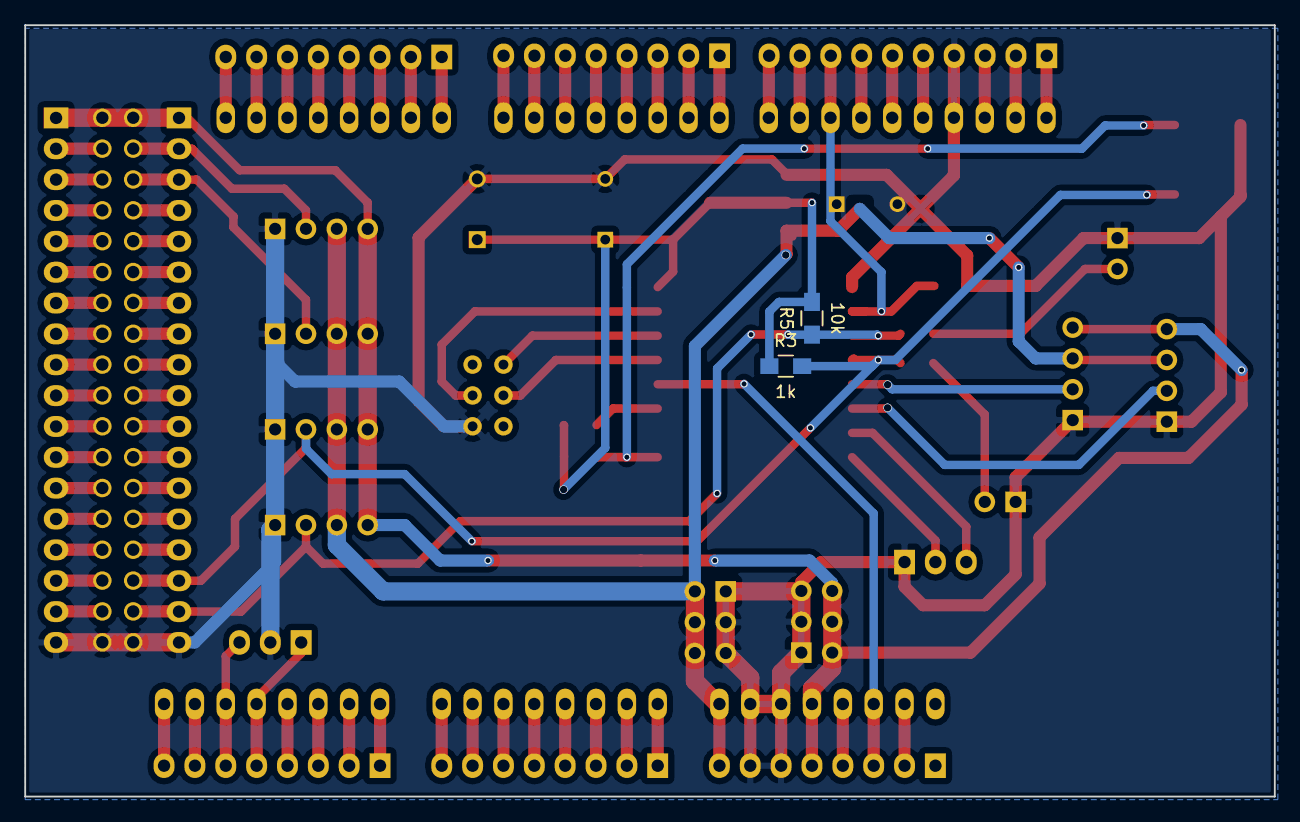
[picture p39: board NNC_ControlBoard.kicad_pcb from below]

Board: 2 copper layers, 102.9 x 63.5 mm, 35 parts (2 on the bottom side), 91 nets.

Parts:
C1, C2: 147uF-550V; C_Radial_D10_L13_P5
C3: C; C_Disc_D6_P5
Control Board: Conditioning Chamber; ARDUINO_DUE_SHIELD
D1: SHOCK LED; Pin_Header_Straight_1x02_Pitch2.54mm
D2: Sound LED; Pin_Header_Straight_1x02_Pitch2.54mm
ESP1: ESP8266-12E; ESP-12E_noBottomPads
ESP-GPIO0: 2; SW_SPST_EVQPE1
ESP-Reset: 1; SW_SPST_EVQPE1
I2C: PWM2; Pin_Header_Straight_1x10
J1: Port 6; Pin_Header_Straight_1x04_Pitch2.54mm
J2: Port 2; Pin_Header_Straight_1x04_Pitch2.54mm
J3: Port 3; Pin_Header_Straight_1x04_Pitch2.54mm
J4: Port 4; Pin_Header_Straight_1x04_Pitch2.54mm
J5: Port 5; Pin_Header_Straight_1x04_Pitch2.54mm
J6: Port 1; Pin_Header_Straight_1x04_Pitch2.54mm
J7: Arduino Vin; Pin_Header_Straight_2x03_Pitch2.54mm
J8: 5V; Pin_Header_Straight_2x03_Pitch2.54mm
P3: Sound (DAC); Pin_Header_Straight_1x03
P4: ESP Serial; Pin_Header_Straight_1x03
P5: DIG1; Pin_Header_Straight_1x18
P6: DIG2; Pin_Header_Straight_1x18
P7: Power; Pin_Header_Straight_1x08
P8: AnalogIN; Pin_Header_Straight_1x08
P9: DAC; Pin_Header_Straight_1x08
P11: PWM1; Pin_Header_Straight_1x08
P12: COM; Pin_Header_Straight_1x08
R1, R2: 150; R_0805_HandSoldering
R3: 1k; R_0805_HandSoldering
R4, R5, R6, R7: 10k; R_0805_HandSoldering
U1: AP1117D33; SOT-223-3_TabPin2

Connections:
/5Voutput: Control Board.5V, Control Board.5V_4, Control Board.5V_5, J1.4, J2.4, J3.4, J4.4, J5.4, J6.4, J8.2, J8.4, J8.6, P5.1, P6.1, P7.5
/Arduino_Vin: C1.1, Control Board.V_IN, J1.3, J2.3, J3.3, J4.3, J5.3, J6.3, J7.2, J7.4, J7.6, P7.8, U1.3
/D22: Control Board.22, J3.2, P5.2
/D23: Control Board.23, P6.2
/D24: Control Board.24, J4.2, P5.3
/D25: Control Board.25, P6.3
/D26: Control Board.26, P5.4
/D27: Control Board.27, P6.4
/D28: Control Board.28, P5.5
/D29: Control Board.29, P6.5
/D30: Control Board.30, P5.6
/D31: Control Board.31, P6.6
/D32: Control Board.32, P5.7
/D33: Control Board.33, P6.7
/D34: Control Board.34, P5.8
/D35: Control Board.35, P6.8
/D36: Control Board.36, P5.9
/D37: Control Board.37, P6.9
/D38: Control Board.38, P5.10
/D39: Control Board.39, P6.10
/D40: Control Board.40, P5.11
/D41: Control Board.41, P6.11
/D42: Control Board.42, P5.12
/D43: Control Board.43, P6.12
/D44: Control Board.44, P5.13
/D45: Control Board.45, P6.13
/D46: Control Board.46, P5.14
/D47: Control Board.47, P6.14
/D48: Control Board.48, P5.15
/D49: Control Board.49, P6.15
/D50: Control Board.50, ESP1.18, ESP-GPIO0.1, J5.2, P5.16, R2.1, R3.2
/D51: Control Board.51, P6.16
/D52: Control Board.52, ESP1.17, J1.2, P5.17, R1.1, R5.1
/D53: Control Board.53, P6.17
/DAC0: Control Board.DAC0, P3.1, P9.5
/DAC1: Control Board.DAC1, P3.3, P9.6
/ESP12Econfig/ESPchpd: ESP1.3, R6.1
/ESP12Econfig/ESPrst: ESP1.1, ESP-Reset.1, R4.2
/ESP12Econfig/VDD3V: C2.1, C3.1, ESP1.8, R3.1, R4.1, R5.2, R6.2, U1.2
/ESP_CS: Control Board.10, ESP1.16, I2C.8, R7.2
/ESP_GPIO16: Control Board.RST, ESP1.4, P7.3
/ESP_I2C_SCL: ESP1.20, J6.2
/ESP_I2C_SDA: ESP1.19, J2.2
/ESP_MISO: Control Board.SP1, ESP1.6
/ESP_MOSI: Control Board.SP4, ESP1.7
/ESP_RX: ESP1.21, P4.3
/ESP_SCK: Control Board.SP3, ESP1.5
/ESP_TX: ESP1.22, P4.2
/GND: C1.2, C2.2, C3.2, Control Board.GND1, Control Board.GND2, Control Board.GND3, Control Board.GND4, Control Board.GND5, Control Board.SP6, D1.1, D2.1, ESP1.15, ESP-GPIO0.2, ESP-Reset.2, I2C.4, J1.1, J2.1, J3.1, J4.1, J5.1, J6.1, J7.1, J7.3, J7.5, J8.1, J8.3, J8.5, P3.2, P4.1, P5.18, P6.18, P7.6, P7.7, R7.1, U1.1
unnamed: D1.2, R1.2
unnamed: D2.2, R2.2
unnamed: Control Board.IO_R, P7.2
unnamed: Control Board.3V3, P7.4
unnamed: Control Board.AD0, P8.1
unnamed: Control Board.AD1, P8.2
unnamed: Control Board.AD2, P8.3
unnamed: Control Board.AD3, P8.4
unnamed: Control Board.AD4, P8.5
unnamed: Control Board.AD5, P8.6
unnamed: Control Board.AD6, P8.7
unnamed: Control Board.AD7, P8.8
unnamed: Control Board.AD8, P9.1
unnamed: Control Board.AD9, P9.2
unnamed: Control Board.AD10, P9.3
unnamed: Control Board.AD11, P9.4
unnamed: Control Board.C_RX, P9.7
unnamed: Control Board.C_TX, P9.8
unnamed: Control Board.SCL1, I2C.1
unnamed: Control Board.SDA1, I2C.2
unnamed: Control Board.AREF, I2C.3
unnamed: Control Board.13, I2C.5
unnamed: Control Board.12, I2C.6
unnamed: Control Board.11, I2C.7
unnamed: Control Board.9, I2C.9
unnamed: Control Board.8, I2C.10
unnamed: Control Board.7, P11.1
unnamed: Control Board.6, P11.2
unnamed: Control Board.5, P11.3
unnamed: Control Board.4, P11.4
unnamed: Control Board.3, P11.5
unnamed: Control Board.2, P11.6
unnamed: Control Board.1, P11.7
unnamed: Control Board.0, P11.8
unnamed: Control Board.14, P12.1
unnamed: Control Board.15, P12.2
unnamed: Control Board.16, P12.3
unnamed: Control Board.17, P12.4
unnamed: Control Board.18, P12.5
unnamed: Control Board.19, P12.6
unnamed: Control Board.20, P12.7
unnamed: Control Board.21, P12.8

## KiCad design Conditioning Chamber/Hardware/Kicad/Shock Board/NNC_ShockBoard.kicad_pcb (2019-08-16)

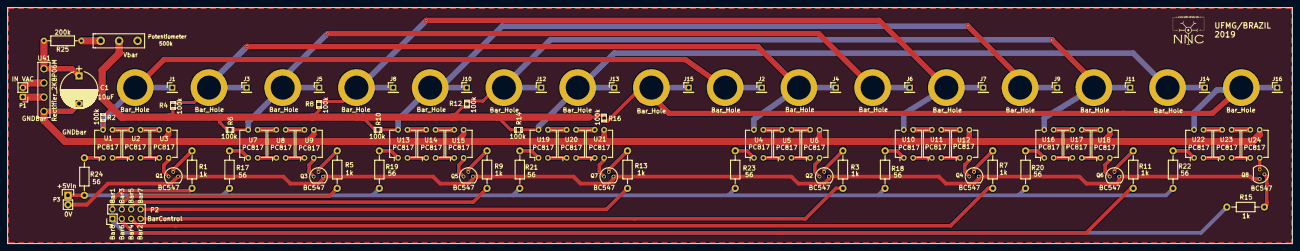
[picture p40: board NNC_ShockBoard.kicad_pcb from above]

Board: 2 copper layers, 348.5 x 64.0 mm, 95 parts (0 on the bottom side), 80 nets.

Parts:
C1: 10uF; CP_Radial_D10.0mm_P7.50mm
J1, J2, J3, J4, J5, J6, J7, J8, J9, J10, J11, J12, J13, J14, J15, J16: Conn_01x01; Pin_Header_Straight_1x01_Pitch2.54mm
P1: IN VAC; Pin_Header_Straight_1x02_Pitch2.54mm
P2: CONN_01X08; Pin_Header_Straight_2x04
P3: 5VDC In; Pin_Header_Straight_1x02
Potentiometer: 500k; Potentiometer_Alps_RK163_Single_Vertical
Q1, Q2, Q3, Q4, Q5, Q6, Q7, Q8: BC547; TO-92_Molded_Narrow
R1, R3, R5, R7, R9, R11, R13, R15: 1k; Resistor_Horizontal_RM10mm
R2, R4, R6, R8, R10, R12, R14, R16: 100k; SMD_0805
R17, R18, R19, R20, R21, R22, R23, R24: 56; Resistor_Horizontal_RM10mm
R25: 200k; R_Axial_DIN0207_L6.3mm_D2.5mm_P10.16mm_Horizontal
U1, U2, U3, U4, U5, U6, U7, U8, U9, U10, U11, U12, U13, U14, U15, U16, U17, U18, U19, U20, U21, U22, U23, U24: PC817; DIP-4_W7.62mm
U25, U26, U27, U28, U29, U30, U31, U32, U33, U34, U35, U36, U37, U38, U39, U40: Bar_Hole
U41: Rectifier_2KBP06M

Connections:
5V_Arduino: P3.1, R17.2, R18.2, R19.2, R20.2, R21.2, R22.2, R23.2, R24.2
/InBarra1: P2.2, R1.2
/InBarra2: P2.7, R3.2
/InBarra3: P2.4, R5.2
/InBarra4: P2.5, R7.2
/InBarra5: P2.6, R9.2
/InBarra6: P2.3, R11.2
/InBarra7: P2.8, R13.2
/InBarra8: P2.1, R15.2
/OutBarra1: J1.1, J2.1, R2.2, U1.4, U25.1, U33.1
/OutBarra2: J3.1, J4.1, R4.2, U4.4, U26.1, U34.1
/OutBarra3: J5.1, J6.1, R6.2, U7.4, U27.1, U35.1
/OutBarra4: J7.1, J8.1, R8.2, U10.4, U28.1, U36.1
/OutBarra5: J9.1, J10.1, R10.2, U13.4, U29.1, U37.1
/OutBarra6: J11.1, J12.1, R12.2, U16.4, U30.1, U38.1
/OutBarra7: J13.1, J14.1, R14.2, U19.4, U31.1, U39.1
/OutBarra8: J15.1, J16.1, R16.2, U22.4, U32.1, U40.1
/Vtrafo+: P1.1, U41.3
/Vtrafo-: P1.2, U41.2
GndArduino: P3.2, Q1.3, Q2.3, Q3.3, Q4.3, Q5.3, Q6.3, Q7.3, Q8.3
GndBarra: C1.2, U3.3, U6.3, U9.3, U12.3, U15.3, U18.3, U21.3, U24.3, U41.4
unnamed: C1.1, R25.2, U41.1
unnamed: Q1.1, U3.2
unnamed: Q1.2, R1.1
unnamed: Q2.1, U6.2
unnamed: Q2.2, R3.1
unnamed: Q3.1, U9.2
unnamed: Q3.2, R5.1
unnamed: Q4.1, U12.2
unnamed: Q4.2, R7.1
unnamed: Q5.1, U15.2
unnamed: Q5.2, R9.1
unnamed: Q6.1, U18.2
unnamed: Q6.2, R11.1
unnamed: Q7.1, U21.2
unnamed: Q7.2, R13.1
unnamed: Q8.1, U24.2
unnamed: Q8.2, R15.1
unnamed: R17.1, U7.1
unnamed: R18.1, U10.1
unnamed: R19.1, U13.1
unnamed: R20.1, U16.1
unnamed: R21.1, U19.1
unnamed: R22.1, U22.1
unnamed: R23.1, U4.1
unnamed: R24.1, U1.1
unnamed: Potentiometer.3, R25.1
unnamed: U1.2, U2.1
unnamed: U1.3, U2.4
unnamed: U2.2, U3.1
unnamed: U2.3, U3.4
unnamed: U4.2, U5.1
unnamed: U4.3, U5.4
unnamed: U5.2, U6.1
unnamed: U5.3, U6.4
unnamed: U7.2, U8.1
unnamed: U7.3, U8.4
unnamed: U8.2, U9.1
unnamed: U8.3, U9.4
unnamed: U10.2, U11.1
unnamed: U10.3, U11.4
unnamed: U11.2, U12.1
unnamed: U11.3, U12.4
unnamed: U13.2, U14.1
unnamed: U13.3, U14.4
unnamed: U14.2, U15.1
unnamed: U14.3, U15.4
unnamed: U16.2, U17.1
unnamed: U16.3, U17.4
unnamed: U17.2, U18.1
unnamed: U17.3, U18.4
unnamed: U19.2, U20.1
unnamed: U19.3, U20.4
unnamed: U20.2, U21.1
unnamed: U20.3, U21.4
unnamed: U22.2, U23.1
unnamed: U22.3, U23.4
unnamed: U23.2, U24.1
unnamed: U23.3, U24.4
Vbarra: Potentiometer.2, R2.1, R4.1, R6.1, R8.1, R10.1, R12.1, R14.1, R16.1

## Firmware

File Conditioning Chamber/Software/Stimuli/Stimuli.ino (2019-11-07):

/*
 * Núcleo de Neurociências - UFMG/Brazil (Universidade Federal de Minas Gerais)
 * 
 * Custom Conditioning Chamber for Classical Fear Conditioning
 * 
 * Sketch for Arduino Due (slave SPI). It receives parameters from ESP8266 (master SPI) and generates configurable sound and shock stimuli patterns.
 * Timer4 and Timer5 are used to control sound and shock temporal patterns.
 * Sound signal is produced by DAC1.
 * Shock signals are produced in 8 digital pins (configurable via code).
 * 
 * Authors: Paulo Aparecido Amaral Júnior  - amaraljr.paulo@gmail.com
 *          Flávio Afonso Gonçalves Mourão - mourao.fg@gmail.com
 *          Márcio Flávio Dutra Moraes     - mfdm@icb.ufmg.br
 *          
 *          2019
 */
 
/*############################################################################################################
        includes.
############################################################################################################*/

#include "Waveforms.h"
#include "DueTimer.h"
#include <SPI.h>
#include <avr/interrupt.h>

/*############################################################################################################
        Defines.
############################################################################################################*/

static BitOrder bitOrder = MSBFIRST;
static int pinSS = 10;    // Slave Select pin for Arduino.
static int pinABORT = 48; // Pin used to Abort experiment (Abort).
static int pinSOUND = 50; // Input pin by which ESP8266 controls SOUND.
static int pinSHOCK = 52; // Input pin by which ESP8266 controls SHOCK.
static int pinTrigger = 53; // Output pin used to generate a reference signal (a square wave) that represents sound modulator.


bool bpinSOUND = false;  // variable used to determine if it's a rising or a falling edge on pinSOUND.
bool bpinSHOCK = false;  // variable used to determine if it's a rising or a falling edge on pinSHOCK.
bool bBarStatus = false; // variable used to track the status of SHOCK (if shock is on or if it's off).

/*  ATENTION!!
    freqModulating must be less than (clock freqModulating)/maxSampleNumModulating
*/
/*############################################################################################################
        Global variables.
############################################################################################################*/
// Variables that ESP8266 will send to ArduinoDue via SPI bus.
/*  ATENTION!!
  carrier_freq must be less than (clock carrier_freq)/maxSampleNumCarrier
  REMEMBER! : maximum feasible frequency is given by the conversor limit: 125kHz
  */
float carrier_freq   = 1000;   // defauilt value for carrier frequency (in Hertz). This variable can be programmed by ESP8266 via webpage -> SPI.
float modulator_freq = 53.71; // default value for modulator frequency (in Hertz). This variable can be programmed by ESP8266 via webpage -> SPI.
float volume_sound   = 100;     // default value for volume sound (in percent). This variable can be programmed by ESP8266 via webpage -> SPI.
int iC = 0;   // Carrier wave counter.
int iM = 0;   // Modulating wave counter
uint32_t DACbuffer[maxSamplesNumCarrier * maxSamplesNumModulating]; // Template of the signal with modulator already calculated.

// SHOCK variables.
float pulse_shockHigh = 10; // default value for the time the bar is tied to GND (in ms). This variable can be programmed by ESP8266 via webpage -> SPI.
float pulse_shockLow  = 10;  // default value for the time that should be waited until reach next bar (in ms). This variable can be programmed by ESP8266 via webpage -> SPI.
float fDeltaT;

int ipulse_shockHigh; // in ms.
int ipulse_shockLow; // in ms.
int iDeltaT;

int iBarPin = 22;
static int iInitialBarPin = 23; // Initial pin for the first bar.
static int MaxNumBarPin   = 8;    // Number of bars.
static int iBarPinStep    = 2;     // Step for bar pins (so we can choose only odd or even pins, for example).
int iCountShockIntervals;

bool bSPIprocessdataOUT = false;
bool bSPIprocessdataIn  = false;
int iSPIdataCountIN  = 0;
int iSPIdataCountOUT = 0;
int iSPIdataMaxOUT   = 0;
byte byteBufferDataIN[500];
byte byteBufferDataOUT[500];
uint32_t uData; // A variable where we copy the content of the SPI Receive Data Register when we have an SPI interrupt.
uint32_t *pointerData;

String strTEMP;

/*############################################################################################################
        Function declarations.
############################################################################################################*/

void slaveBegin(uint8_t _pin);
void FUNCAO_INTERRUPT();
void ProcessIncomingData();
void bars(bool bStatusiBarPin);
void carrier();
void modulating();
void pinSOUND_rising();
void pinSOUND_falling();
void pinSHOCK_rising();
void pinSHOCK_falling();
void ProgramSound();
void ProgramShock();
void Abort();

/*############################################################################################################
        Setup
############################################################################################################*/

void setup()
{
  // Configure SPI communication.
  slaveBegin(pinSS);

  pinMode(pinABORT, INPUT);
  pinMode(pinSOUND, INPUT);
  pinMode(pinSHOCK, INPUT);
  pinMode(pinTrigger, OUTPUT);
  digitalWrite(pinTrigger, LOW);
  
  // Programming pins that control bars potentials
  for (int i = 0; i < MaxNumBarPin; i++)
  {
    pinMode((iInitialBarPin + i * iBarPinStep), OUTPUT);
    digitalWrite((iInitialBarPin + i * iBarPinStep), LOW);
  }

  // Timer4 produces carrier signal and timer5 modulates carrier signal
  Timer4.attachInterrupt(carrier);
  Timer5.attachInterrupt(modulating);

  analogWriteResolution(12);
  analogWrite(DAC1, 0); // Configure DAC communication with analogWrite's built-in parameters

  ProgramSound(); //Program template signal for SOUND.
}

/*############################################################################################################
        Loop
############################################################################################################*/

void loop()
{
  if (bpinSOUND != digitalRead(pinSOUND)) // check if pinSOUND has changed state.
  {
    if (bpinSOUND) pinSOUND_falling(); // check if it was a falling edge.
    else pinSOUND_rising();            

    bpinSOUND = !bpinSOUND; // toggle bpinsSOUND, since pinSOUND changed state.
  }

  if (bpinSHOCK != digitalRead(pinSHOCK)) // check if pinSHOCK has changed state.
  {
    if (bpinSHOCK) pinSHOCK_falling();    // check if it was a falling edge.
      else pinSHOCK_rising();             
    if (ipulse_shockHigh > 0) bpinSHOCK = !bpinSHOCK; // we check if pulse_shockHigh > 0 before writing TRUE/FALSE to bpinSHOCK. Else, bpinSHOCK will always be false.
  }

  if (bpinSHOCK) bars(bBarStatus); // if bpinSHOCK is TRUE, shock must be turned on (this is made in bars() function).

  //SerialComandCheck();
  if (bSPIprocessdataIn) ProcessIncomingData();

}

/*############################################################################################################
        slaveBegin. Programm Arduino Due as a slave SPI.
############################################################################################################*/

void slaveBegin(uint8_t _pin)
{
  SPI.begin(_pin);
  REG_SPI0_CR = SPI_CR_SWRST;      // reset SPI
  REG_SPI0_CR = SPI_CR_SPIEN;      // enable SPI
  REG_SPI0_MR = SPI_MR_MODFDIS;    // slave and no modefault
  REG_SPI0_CSR = SPI_MODE0|(0x80); // DLYBCT=0, DLYBS=0, SCBR=0, 16 bit transfer

  //REG_SPI0_IER=SPI_IER_RDRF; // Setting Interrupt Enable Flag Register to 1???

  delay(1000);
  
  // Configures interruption whenever master SPI sends a message.
  int intNum = digitalPinToInterrupt(_pin); // _pin (SPI slave select) is used to generate interrupts.
  if (intNum != NOT_AN_INTERRUPT) 
  {
    SPI.usingInterrupt(intNum); // uses slave select pin to trigger an interrupt service routine (FUNCAO_INTERRUPT).
    attachInterrupt(intNum, FUNCAO_INTERRUPT, RISING); // Slave select rising indicates that SPI transaction in done and data can be processed.
  }
}

/*############################################################################################################
    SPI Transmission/reception complete ISR
    
    SPI COMUNICATION FROM/TO MASTER: Our protocol.

        0xA0A0 is the command word sent by ESP8266 that indicates SPI data should be processed.
        0x0010 is the command word sent by ESP8266 that indicates control variables should be programmed.
          (values for carrier_freq, modulator_freq, pulse_shockHigh and pulse_shockLow should be sent by ESP8266 after 0x0010 command)
        0x10FF is the command word sent by Arduino indicating that the values for the control variables were all received.
        0x1000 is the command word sent by Arduino indicating that the values for the control variables were not received.
        0x1A00 is the command word sent by ESP8266 indicating to ABORT experiment.

    SPI Registers and Commands:
        REG_SPI0_SR - SPI Status Register
        REG_SPI0_RDR - SPI Receive Data Register
        SPI_SR_RDRF - Receive Data Register Full
        SPI_SR_TDRE - Transmit Data Register Empty
        
############################################################################################################*/

void FUNCAO_INTERRUPT()
{
    while ((REG_SPI0_SR & SPI_SR_RDRF) != 0) // wait for SPI data is available
      {
      uData = REG_SPI0_RDR; // The registry is a uint32_t 32bit word
        if (bitOrder == LSBFIRST) uData = __REV(__RBIT(uData));
      byteBufferDataIN[iSPIdataCountIN]= (uData & 0xFF);        // copy the first byte received to byteBufferDataIN.
      byteBufferDataIN[iSPIdataCountIN+1]= (uData & 0xFF00)>>8; // copy the second byte received to byteBufferDataIN.
      iSPIdataCountIN+=2;

      if (uData==0xA0A0) bSPIprocessdataIn=true; // status of bSPIprocessdataIn variable is checked in main loop. Fim de comando.

      if (((REG_SPI0_SR & SPI_SR_TDRE) != 0) && bSPIprocessdataOUT) // checking if we have to send data
        {
          pointerData= (uint32_t *) (byteBufferDataOUT +iSPIdataCountOUT);
          REG_SPI0_TDR = *pointerData;
          iSPIdataCountOUT+=2;
          if (iSPIdataCountOUT>=iSPIdataMaxOUT) // If at the end, finished reading.
              {
                iSPIdataCountOUT=0;
                bSPIprocessdataOUT=false;
                iSPIdataMaxOUT=0;
              }
        }
      }
}
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

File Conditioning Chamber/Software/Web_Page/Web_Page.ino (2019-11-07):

/*
 * Núcleo de Neurociências - UFMG/Brazil (Universidade Federal de Minas Gerais)
 * 
 * Custom Conditioning Chamber for Classical Fear Conditioning
 * 
 * Sketch for Arduino Due (slave SPI). It receives parameters from ESP8266 (master SPI) and generates configurable sound and shock stimuli patterns.
 * Timer4 and Timer5 are used to control sound and shock temporal patterns.
 * Sound signal is produced by DAC1.
 * Shock signals are produced in 8 digital pins (configurable via code).
 * 
 * Authors: Paulo Aparecido Amaral Júnior  - amaraljr.paulo@gmail.com
 *          Flávio Afonso Gonçalves Mourão - mourao.fg@gmail.com
 *          Márcio Flávio Dutra Moraes     - mfdm@icb.ufmg.br
 *          
 *          2019
 */
 
/*############################################################################################################
        Includes.
############################################################################################################*/
  
  #include <ESP8266WiFi.h> // Link for ESP8266 library download: https://github.com/esp8266/Arduino
  #include <ESP8266WebServer.h>
  #include <ESP8266mDNS.h>
  
  #include <SPI.h>
  #include <EEPROM.h>
  
  #include "user_interface.h"
  #include "Web_Page.h"

/*############################################################################################################
        Global variables.
############################################################################################################*/
  
  const char *ssid = "ConditioningCage";
  const char *password = "0112358132"; // Fibonacci
  IPAddress myIP;
  ESP8266WebServer server ( 80 );

/*############################################################################################################
        Function declarations.
############################################################################################################*/
  
  void handleRoot();
  void Programar();
  void handleNotFound();

/*############################################################################################################
        Setup.
############################################################################################################*/
  void setup ( void ) 
  {
    // Uncommenting Serial.begin() and all Serial.println() lines may help troubleshooting this sketch.
    // Configure UART communication
	  //Serial.begin ( 115200 );

    pinMode ( ArduinoDueSkinner->pinABORT, OUTPUT );
    digitalWrite ( ArduinoDueSkinner->pinABORT, LOW );
    pinMode ( ArduinoDueSkinner->pinSOUND, OUTPUT );
    digitalWrite ( ArduinoDueSkinner->pinSOUND, LOW );
    //pinMode ( ArduinoDueSkinner->pinSOUNDnot, OUTPUT );
    //digitalWrite ( ArduinoDueSkinner->pinSOUNDnot, HIGH );
    pinMode ( ArduinoDueSkinner->pinSHOCK, OUTPUT );
    digitalWrite ( ArduinoDueSkinner->pinSHOCK, LOW );

    // Waiting 1 second before reset Arduino
    delay(1000);
    pinMode (ArduinoDueSkinner->pinRSTarduino,OUTPUT);
    digitalWrite ( ArduinoDueSkinner->pinRSTarduino, LOW );
    delay(100);
    digitalWrite ( ArduinoDueSkinner->pinRSTarduino, HIGH );
  
    // Configure SPI communication.
    SPI.begin ();
    SPI.setBitOrder(MSBFIRST);
    SPI.setDataMode(SPI_MODE0); 
    SPI.setClockDivider(SPI_CLOCK_DIV16);
    //SPI.setClockDivider(SPI_CLOCK_DIV2); 
                                         /* SPI_CLOCK_DIV2    0x00101001 //8 MHz
                                            SPI_CLOCK_DIV4    0x00241001 //4 MHz
                                            SPI_CLOCK_DIV8    0x004c1001 //2 MHz
                                            SPI_CLOCK_DIV16   0x009c1001 //1 MHz
                                            SPI_CLOCK_DIV32   0x013c1001 //500 KHz
                                            SPI_CLOCK_DIV64   0x027c1001 //250 KHz
                                            SPI_CLOCK_DIV128  0x04fc1001 //125 KHz */
    SPI.setHwCs(true); // setHwCs(true) sets ESP8266 as MASTER. setHwCs(false) sets ESP8266 as SLAVE.

    // Configure WiFI
    WiFi.mode(WIFI_AP);
    WiFi.softAP(ssid, password);
    myIP = WiFi.softAPIP();
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

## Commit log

2019-08-16 Update 16-08-19
    [Botton.stl, Chamber.stl, Conditioning_full_parts.skp, Conditioning_full_parts.stl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]
2019-11-19 Update 19-11-19
    - Control box New Version (2.0). New box Design and Audio Amplifier (LM386) add to the project.
    - Article published in Frontiers in Neuroscience | www.frontiersin.org
    [Control_box.stl, Control_box_floor.stl, Control_box_roof.stl, Power_supply_holder.stl]
2019-11-19 Update 19-11-19
    [Botton.stl, Chamber.stl, Conditioning_full_parts.skp, Conditioning_full_parts.stl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]
